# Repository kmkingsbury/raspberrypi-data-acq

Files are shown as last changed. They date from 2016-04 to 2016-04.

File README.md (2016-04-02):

# raspberrypi-data-acq

Scripts for using a Raspberry Pi 2 B+ as a data acquisition box.
Instructable for this project: http://www.instructables.com/id/Scrappy-Science-Caddy

## Supported Platforms

Raspberry Pi 2 B+

## Attributes

<table>
  <tr>
    <th>Key</th>
    <th>Type</th>
    <th>Description</th>
  </tr>
  <tr>
    <td><tt>-s,--sleep</tt></td>
    <td>Float</td>
    <td>Time to sleep between measurements. Like a polling frequency, if set to 1 it will take a new measurement roughly every second, .5 is every half second, etc.</td>
  </tr>
  <tr>
    <td><tt>-n,--channels</tt></td>
    <td>Integer</td>
    <td>Number of channels to record</td>
  </tr>
  <tr>
    <td><tt>-g,--gnuplot</tt></td>
    <td>Switch</td>
    <td>Output the file in a GNUPlot-friendly format rather than a CSV</td>
  </tr>
  <tr>
    <td><tt>-c,--config</tt></td>
    <td>String</td>
    <td>Use Config file, default config.ini</td>
  </tr>
  <tr>
    <td><tt>-o,--outfile</tt></td>
    <td>String</td>
    <td>CSV Output file to use</td>
  </tr>
  <tr>
    <td><tt>-d,--debug</tt></td>
    <td>String</td>
    <td>Output extra messages for debugging</td>
  </tr>
  <tr>
    <td><tt>-t,--type</tt></td>
    <td>String</td>
    <td>Data Type for each channel. (See explanation below)</td>
  </tr>
</table>

### Data Type

Data type is the type of data coming on the channel, automatic conversions can ve done. If none specified then it uses 'raw' as the default which is the straight reading from the GPIO pin (values 0-1024). Other supported types are 'ctemp' which converts the value to a Temperature in Celsius, and 'ftype' which converts the value to a Temperature in Fahrenheit. Data types can be mixed and matched, assume a three channel setup, you could do raw for the first channel, ctemp for the 2nd and ftemp for the third. Such a setup would look like:

```python
sudo python collectdata.py -c 3 -t raw ctemp ftemp
```

## Usage

Basic Program flow:
* Specify the number of channels, output file, and/or any other parameters.
* The script runs indefinitely logging data to the output file and displaying on screen
* Use Ctrl-C to quit.

### python collectdata.py

Run normally using all defaults:
```python
raspberrypi-data-acq $ sudo python ./collectdata.py
```

Record data from 4 different sources:
```python
raspberrypi-data-acq $ sudo python ./collectdata.py -c 4
```

Record data from 4 different sources at 1/10 of a second intervals:
```python
raspberrypi-data-acq $ sudo python ./collectdata.py -c 4 -s 0.1
```

Record data from 4 different sources at 1/10 of a second intervals, output to mydata.csv in the home directory:
```python
raspberrypi-data-acq $ sudo python ./collectdata.py -c 4 -s 0.1 -o ~/mydata.csv
```

Record data from 3 different sources the first as raw data, Celsius Temperature for the 2nd and 3rd:
```python
raspberrypi-data-acq $ sudo python ./collectdata.py -c 3 -t raw ctemp ctemp
```

## Pi Configuration
usbmount is used to automount a USB stick when it is plugged in, install the package:
```
sudo apt-get install usbmount
```

Configuration in /etc/usbmount/usbmount.conf

Files are then by default dropped in ```/media/usb0```

## License and Authors

Author:: Kevin Kingsbury (@kmkingsbury)

Apache 2.0

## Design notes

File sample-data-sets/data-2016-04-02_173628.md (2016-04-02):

Raw parameters: collectdata.py -n 4 -s .1 -g
Namespace parameters: collectdata.py Namespace(channels=[4], config=None, debug=False, gnuplot=True, outfile=None, sleep=[0.1], type=None)
Config file: config.ini
Channels: 4
Sleeptime: 0.1
Types: [raw, raw, raw, raw]
DataTypes: [raw, raw, raw, raw]
Samples: 20607
ButtonEvents: 0
Avg: [121, 132, 158, 176]
Maxs: [327, 329, 377, 405]
Mins: [0, 0, 0, 0]

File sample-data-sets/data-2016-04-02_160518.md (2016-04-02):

Raw parameters: collectdata.py -n 1 -s .25 -g
Namespace parameters: collectdata.py Namespace(channels=[1], config=None, debug=False, gnuplot=True, outfile=None, sleep=[0.25], type=None)
Config file: config.ini
Channels: 1
Sleeptime: 0.25
Types: [raw]
DataTypes: [raw]
mk3 Event: 2016-04-02 16:17:24.08, 318
mk2 Event: 2016-04-02 16:24:20.52,411
mk1 Event: 2016-04-02 16:23:36.10,402
mk4 Event: 2016-04-02 16:33:35.97,428
mk4 Event: 2016-04-02 16:57:30.68,365
Samples: 11917
ButtonEvents: 5
Avg: [363]
Maxs: [468]
Mins: [217]

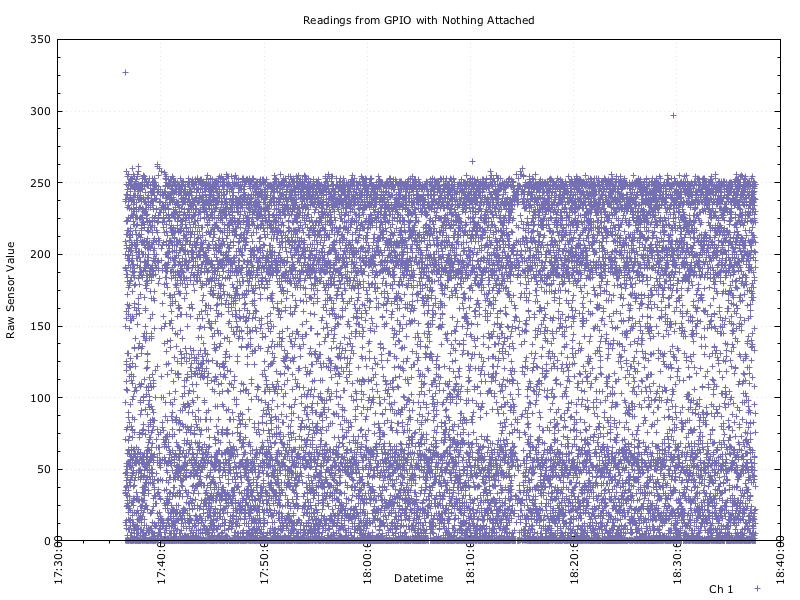
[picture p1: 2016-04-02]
sample-data-sets/data-2016-04-02_173628.gnuplot_raw.png

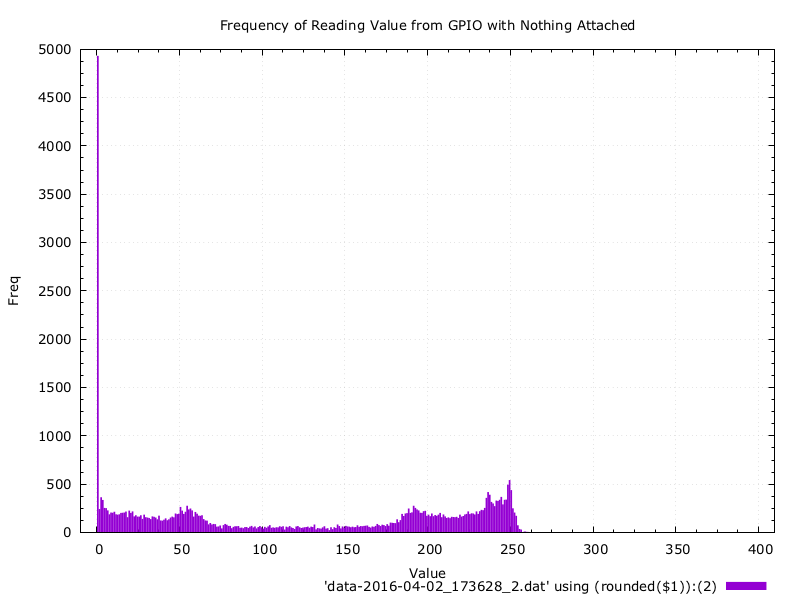
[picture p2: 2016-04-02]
sample-data-sets/data-2016-04-02_173628.gnuplot_freq.png

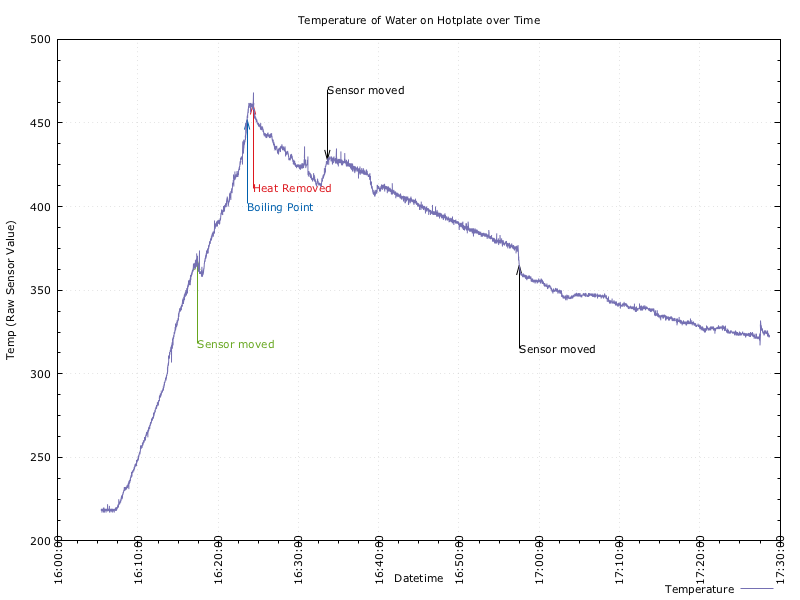
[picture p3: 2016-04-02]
sample-data-sets/data-2016-04-02_160518.gnuplot.png

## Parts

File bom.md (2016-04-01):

# Bill of Materials

## Hardware
Item|Count|Price|Url / Source
----|-----|-----|------------
Red Oak Hobby Board (Common: 1/4-in x 6-in x 2-Ft; Actual: 0.25-in x 5.5-in x 2-ft)| 1|$6.47|http://www.lowes.com/pd_9365-34050-OAK6X140-U2S___
Plexiglass sheet |1|$2.97|http://www.lowes.com/pd_55844-1638-11G0810A___
Motherboard mounts|8|$7.90 (for 50)|http://amzn.com/B00008VF6K
Round-Head Standard (SAE) Machine Screws #4 & #6 size |~16|$1.24 for 12 |http://www.lowes.com/pd_62045-37672-491276___
Nylon Standoffs|8|~$2.00|Local Big Box Store

## Electronics
Item|Count|Price|Url / Source
----|-----|-----|------------
Raspberry Pi 2 or 3 |1|$37.99 or $45.97|http://amzn.com/B018L66L9S or http://amzn.com/B01CD5VC92
MCP3008 |1|$3.75 |https://www.adafruit.com/product/856
Push Buttons (green, black, red, blue)|4|$6.98 (for 10 in one color)| http://amzn.com/B015CYF3VE, http://amzn.com/B015CYHS3U, http://amzn.com/B015CY8WJ4, http://amzn.com/B017EFQD6S
5 way navigation button |1|$2.95 | https://www.adafruit.com/products/504
Poteniometer |1 | $1.25|https://www.adafruit.com/products/356
LCD 16x2 Char Display |1|$15.95 |https://www.sparkfun.com/products/709
3 pin polarized connector (Male & Female) | 4| $0.50| http://www.kr4.us/polarized-connectors-housing-3-pin.html
Optional: 16 Pins Round Hole DIP IC Chip Socket Adaptor | 1| $5.16 (for 10)|http://amzn.com/B00X77NYG0
Optional: PCB Board 16 Pin |1 | 7.11 (for 20)| http://amzn.com/B01173BKZW (I got mine for $2 at Radioshack)

----
## Assorted Odds &amp; Ends on Hand
* Hook-up Wire
* Paint & Primer (or wood stain)
* Wood Glue
* Small nails
* Wire shrink wraps
* Electrical Tape
* Old IDE Cable for pins (http://amzn.com/B002BBNEOU)
* Motherboard mounts (also listed above)
* Screws #4 & #6 (also listed above)

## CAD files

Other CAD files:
drawings/data-container.skp

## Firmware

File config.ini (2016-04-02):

[general]
# include trailing slash
filesavedir = /media/usb0/

[AD MCP3008]
# Analog to Digital Converter Chip MCP3008
SPICLK = 18
SPIMISO = 23
SPIMOSI = 24
SPICS = 25

[menu]
# 5-way navigation (next to LCD)
up =  22
down = 27
left = 17
right = 7
select = 4

[buttons]
# Push buttons on top: Red, Green, Blue, Black
Mk1 = 13
MK2 = 6
Mk3 = 5
Mk4 = 8

[lcd]
# LCD Control Pins
LCD_RS = 19
LCD_E  = 26
LCD_D4 = 20
LCD_D5 = 16
LCD_D6 = 12
LCD_D7 = 21
LCD_WIDTH = 16
# Maximum characters per line
LCD_CHR = true
LCD_CMD = false
# LCD RAM address for the 1st line
LCD_LINE_1 = 0x80
# LCD RAM address for the 2nd line
LCD_LINE_2 = 0xC0

# Timing constants
E_PULSE = 0.0005
E_DELAY = 0.0005

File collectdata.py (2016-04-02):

#! /usr/bin/python
# Based off the daemon code written by Dan Mandle http://dan.mandle.me September 2012
# LCD parts from 16x2 LCD Test Script
# which is written by : Matt Hawkins 06/04/2015 (http://www.raspberrypi-spy.co.uk/)
#
# The Rest by Kevin Kingsbury: https://github.com/kmkingsbury
# License: Apache 2.0

import os
from daemon import Daemon
from subprocess import *
import RPi.GPIO as GPIO

import time
from time import gmtime, strftime
import threading
#import yaml
import csv
#import rrdtool
import sys, argparse
import ConfigParser
import re

from ssc_lcd import *

version = 0.1

class SmartFormatter(argparse.HelpFormatter):

    def _split_lines(self, text, width):
        # this is the RawTextHelpFormatter._split_lines
        if text.startswith('R|'):
            return text[2:].splitlines()
        return argparse.HelpFormatter._split_lines(self, text, width)

GPIO.setwarnings(False)
GPIO.setmode(GPIO.BCM)


# Parse Args:
def mainargs(argv):
  parser = argparse.ArgumentParser(description='Collects Data on a Raspberry Pi 2 B+.',
  formatter_class=SmartFormatter, epilog="Example 3 channel of raw and 2 Celsius temperature:\n sudo python ./collectdata.py -n 3 -t raw ctemp ctemp"
  )
  parser.add_argument('-s', '--sleep', type=float, nargs=1, required=False,
                   help='Time (seconds) to sleep between measurements')
  parser.add_argument('-n', '--channels', type=int, nargs=1, required=False,
                 help='Number of channels to record')
  parser.add_argument('-o', '--outfile', nargs=1, required=False,
               help='Outfile to use')
  parser.add_argument('-c', '--config', nargs=1, required=False,
                            help='Config File to use')
  parser.add_argument('-g', '--gnuplot', action='store_true', required=False,
               help='Print the outputfile in gnuplot format (tabs) instead of CSV')
  parser.add_argument('-d', '--debug', action='store_true', required=False,
               help='Print Debug messages')
  parser.add_argument('-t', '--type', type=str, nargs='+', required=False, choices=['raw', 'ctemp', 'ftemp'],
               help="R|Datatypes to record space separate.\n"
         " raw = raw values (0 to 1024, default value)\n"
         " ctemp = Temperature (Celsius)\n"
         " ftemp = Temperature (Fahrenheit)")
  args = parser.parse_args()
  return args

def run_cmd(cmd):
    p = Popen(cmd, shell=True, stdout=PIPE)
    output = p.communicate()[0]
    return output

def CtoF(temp):
	temp = (temp * (9.0/5.0))+32.0
	return round(temp,2)

def ConvertTemp(data):
	temp = ((data - 100)/10.0) - 40.0
	temp = round(temp,4)
	return temp

def ConvertmVolts(data):
	volts = (data * 3300.0) / 1023.0
	volts = round(volts, 4)
	return volts

def buttonEventHandler (pin):
    global config, fpmeta, displaymode, MKbuttonevents, data
    print "handling button event: "+str(pin)

    # Match Buttons, Log event:
    for (each_key, each_val) in config.items('buttons'):
      if pin == int(each_val):
        #print "here.\n"
        timenow = highrestime()
        fpmeta.write(""+each_key + ' Event: '+ timenow + ', '.join(map(str, data)) + '\n')
        MKbuttonevents += 1
        return

    # Match Menu
    if pin == config.getint('menu', 'up'):
      displaymode = 'Max'
      return
    elif pin == config.getint('menu', 'down'):
      displaymode = 'Min'
      return
    elif pin == config.getint('menu', 'right'):
      displaymode = 'Avg'
      return
    elif pin == config.getint('menu', 'left'):
      displaymode = 'Dev'
      return
    elif pin == config.getint('menu', 'select'):
      displaymode = 'Reg'
      return


def highrestime():
    global time
    mynow = str(time.time())
    timenow = strftime("%Y-%m-%d %H:%M:%S", gmtime())
    dec = mynow.split(".")
    #this is a dumb way to get zero padded decimal seconds
    timenow += "."+format(float("."+dec[1]), '.2f').split('.')[1]
    return timenow

# read SPI data from MCP3008 chip, 8 possible adc's (0 thru 7)
def readadc(adcnum, clockpin, mosipin, misopin, cspin):
        if ((adcnum > 7) or (adcnum < 0)):
                return -1
        GPIO.output(cspin, True)

        GPIO.output(clockpin, False)  # start clock low
        GPIO.output(cspin, False)     # bring CS low

        commandout = adcnum
        commandout |= 0x18  # start bit + single-ended bit
        commandout <<= 3    # we only need to send 5 bits here
        for i in range(5):
                if (commandout & 0x80):
                        GPIO.output(mosipin, True)
                else:
                        GPIO.output(mosipin, False)
                commandout <<= 1
                GPIO.output(clockpin, True)
                GPIO.output(clockpin, False)

        adcout = 0
        # read in one empty bit, one null bit and 10 ADC bits
        for i in range(12):
                GPIO.output(clockpin, True)
                GPIO.output(clockpin, False)
                adcout <<= 1
                if (GPIO.input(misopin)):
                        adcout |= 0x1

        GPIO.output(cspin, True)

        adcout >>= 1       # first bit is 'null' so drop it
        return adcout

rawargs = ' '.join (sys.argv)
#print "Raw: "+ rawargs

# Parse Args, handle options
args = mainargs(sys.argv[1:])

# Config File
configfile = 'config.ini'
if args.config: config = args.config[0]
if args.debug: print "Config file: " + str(configfile)

config = ConfigParser.ConfigParser()
config.read(configfile)

# Sleep
sleeptime = 1;
if args.sleep: sleeptime = args.sleep[0]
if args.debug: print "Sleep time: " + str(sleeptime)

# Channels
channels = 4;
if args.channels: channels = int(args.channels[0])
if args.debug: print "Channels: " + str(channels)

# Outfile
outfile = config.get('general', 'filesavedir', 0) + "data-"+strftime("%Y-%m-%d_%H%M%S", gmtime())+".csv"
if args.gnuplot: outfile = "data-"+strftime("%Y-%m-%d_%H%M%S", gmtime())+".dat"
if args.outfile: outfile = args.outfile[0]
if args.debug: print "Outfile: " + outfile
filewoext = re.split('(.*)\.\w', outfile)
#print filewoext[1]
metafile = filewoext[1] +".md"
if args.debug: print "Metafile: "+ metafile

# This is all matching the datatypes and getting the correct array sizes
types = []
if args.type:
  types = args.type
else:
  types = ['raw'] * channels

datatype = ['raw'] * 8
if args.debug: print "Len:" + str(len(types))
if len(types) != channels:
  for val in range(0,channels):
    if args.debug: print "Vals: " + str(val)
    try:
      #print "DT (" + str(val) + "):" + str(datatype[val-1] )
      if args.debug: print "T (" + str(val) + "):" + str(types[val] )

      datatype[(val)] = types[val]
    except IndexError:
      datatype.append('raw')
elif len(types) > channels:
  datatype = types[:(channels)]
else:
  datatype = types[:(channels)]

# make final correct size
datatype = datatype[:(channels)]
if args.debug: print "Types: " + '[%s]' % ', '.join(map(str, types))
if args.debug: print "DataTypes: " + '[%s]' % ', '.join(map(str, datatype))


# put in top level scope, reset in the loop

if __name__ == '__main__':

  runner = True

  print 'sys:'+ str(sys.argv[0]) + ' ' + str(args)

  # Logger open CSV
  fp = open(outfile, 'w')
  fpmeta = open(metafile, 'w')
  fpmeta.write('Raw parameters: '+rawargs+ '\n')
  fpmeta.write('Namespace parameters: '+ str(sys.argv[0]) + ' ' + str(args) + '\n')
  fpmeta.write('Config file: ' + str(configfile) + '\n')
  fpmeta.write('Channels: ' + str(channels)+ '\n')
  fpmeta.write('Sleeptime: ' + str(sleeptime)+ '\n')
  fpmeta.write("Types: " + '[%s]' % ', '.join(map(str, types))+ '\n')
  fpmeta.write("DataTypes: " + '[%s]' % ', '.join(map(str, datatype))+ '\n')

  fp.write('# Input parameters: '+ str(sys.argv[0]) + ' ' + str(args) + '\n')
  fp.write('# Datetime\t\t')
  for x in range(1, channels):
      fp.write("\t Ch"+str(x))
  fp.write("\n")

  cvs = None
  if args.gnuplot == False:
    writer = csv.DictWriter(fp, fieldnames = ['datetime']+ datatype, delimiter=',')
    writer.writeheader()
    csv = csv.writer(fp, delimiter=',', quoting=csv.QUOTE_ALL)
  else:
    csv = csv.writer(fp, delimiter="\t", quoting=csv.QUOTE_NONNUMERIC, quotechar='\'')

  # set up the SPI interface pins
  GPIO.setup(config.getint('AD MCP3008', 'SPIMOSI'), GPIO.OUT)
  GPIO.setup(config.getint('AD MCP3008', 'SPIMISO'), GPIO.IN)
  GPIO.setup(config.getint('AD MCP3008', 'SPICLK'), GPIO.OUT)
  GPIO.setup(config.getint('AD MCP3008', 'SPICS'), GPIO.OUT)

  GPIO.setup(config.getint('lcd', 'LCD_RS'), GPIO.OUT)
  GPIO.setup(config.getint('lcd', 'LCD_E'), GPIO.OUT)
  GPIO.setup(config.getint('lcd', 'LCD_D4'), GPIO.OUT)
  GPIO.setup(config.getint('lcd', 'LCD_D5'), GPIO.OUT)
  GPIO.setup(config.getint('lcd', 'LCD_D6'), GPIO.OUT)
  GPIO.setup(config.getint('lcd', 'LCD_D7'), GPIO.OUT)


  lcd_init(config)
  lcd_string(config,"Scrapy Science",0x80)
  lcd_string(config,"Caddy v"+str(version),0xC0)
  time.sleep(2)
  lcd_string(config,strftime("%Y-%m-%d %H:%M", gmtime()),0x80)
  cmd = "ip addr show wlan0 | grep inet | awk '{print $2}' | cut -d/ -f1 | head -n 1"
  ipaddr = run_cmd(cmd).strip()
  lcd_string(config,ipaddr,0xC0)
  time.sleep(2)

  # Button Setups:
  for (each_key, each_val) in config.items('menu'):
    GPIO.setup(int(each_val), GPIO.IN, pull_up_down=GPIO.PUD_UP)
    GPIO.add_event_detect(int(each_val),GPIO.FALLING, callback=buttonEventHandler, bouncetime=300)

  for (each_key, each_val) in config.items('buttons'):
    GPIO.setup(int(each_val), GPIO.IN, pull_up_down=GPIO.PUD_UP)
    GPIO.add_event_detect(int(each_val), GPIO.FALLING, callback=buttonEventHandler, bouncetime=300)

  # Reset count
  samplecount = 0
  MKbuttonevents = 0
  lastgmt = 0
  displaymode = 'Reg'
  sums = [0,0,0,0];
  mins = [None, None, None, None]
  maxs = [None, None, None, None]
  avgs = [0,0,0,0];
  try:
    while (runner == True):
      #It may take a second or two to get good data

      timenow = highrestime()
      data = [ timenow,0,0,0,0,0,0,0,0 ]
      rawvalues = [0] * 8
      values = [0] * 8
      for val in range(0,channels):
       if args.debug: print "Val:" + str(val)
       rawvalues[val] = readadc(val,
        config.getint('AD MCP3008', 'SPICLK'),
        config.getint('AD MCP3008', 'SPIMOSI'),
        config.getint('AD MCP3008', 'SPIMISO'),
        config.getint('AD MCP3008', 'SPICS'))

       # Convert raw value to something else if specificed in type option.
       if datatype[(val)] == 'ftemp':
         values[val] = CtoF(ConvertTemp(ConvertmVolts(rawvalues[val])))
       elif datatype[(val)] == 'ctemp':
         values[val] = ConvertTemp(ConvertmVolts(rawvalues[val]))
       else:
         values[val] = rawvalues[val]
       data[(val+1)] = values[val]
       sums[val] += values[val]
       if mins[val] == None : mins[val] = values[val]
       if maxs[val] == None : maxs[val] = values[val]
       if values[val] < mins[val]: mins[val] = values[val]
       if values[val] > maxs[val]: maxs[val] = values[val]
       avgs[val] = sums[val]/(samplecount+1)
      # Prepare and Print the raw values if debug flag set
      rawline = 'Raw '
      for val in range(0,channels):
        rawline += "V"+str(val+1)+":"+ str(rawvalues[val]) + " "
      if args.debug: print rawline
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

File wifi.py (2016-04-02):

import ConfigParser
import os
import time

from time import gmtime, strftime
from subprocess import *
import RPi.GPIO as GPIO

from ssc_lcd import *

configfile = 'config.ini'

config = ConfigParser.ConfigParser()
config.read(configfile)

GPIO.setwarnings(False)
GPIO.setmode(GPIO.BCM)
GPIO.setup(config.getint('lcd', 'LCD_RS'), GPIO.OUT)
GPIO.setup(config.getint('lcd', 'LCD_E'), GPIO.OUT)
GPIO.setup(config.getint('lcd', 'LCD_D4'), GPIO.OUT)
GPIO.setup(config.getint('lcd', 'LCD_D5'), GPIO.OUT)
GPIO.setup(config.getint('lcd', 'LCD_D6'), GPIO.OUT)
GPIO.setup(config.getint('lcd', 'LCD_D7'), GPIO.OUT)


def run_cmd(cmd):
    p = Popen(cmd, shell=True, stdout=PIPE)
    output = p.communicate()[0]
    return output

try:
    while (1 == 1):
      lcd_string(config,strftime("%Y-%m-%d %H:%M", gmtime()),0x80)
      cmd = "ip addr show wlan0 | grep inet | awk '{print $2}' | cut -d/ -f1 | head -n 1"
      ipaddr = run_cmd(cmd).strip()
      lcd_string(config,ipaddr,0xC0)
      time.sleep(2)

except (KeyboardInterrupt, SystemExit): #when you press ctrl+c
  print "\nKilling Thread..."
  lcd_byte(config,0x01, config.getboolean('lcd', 'LCD_CMD'))
  lcd_string(config,"Goodbye",0x80)
  lcd_string(config,ipaddr,0xC0)
  GPIO.cleanup()
  exit();

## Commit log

2015-09-15 Added current sketchup drawing
    [data-container.skp]
2015-09-15 Added schematic folder and Fritzing Diagram
    [Data-Acq.fzz]
2015-09-26 Pin setup
2016-02-11 Expanded the help file, added sample data sets.
    [temp-temp-soil.csv, temp-temp-soil2.csv]
2016-02-18 Updated drawing, added objects
    [data-container.skp]
2016-03-17 Updated drawing, added wiring and buttons to schematic
    [Data-Acq.fzz, data-container.skp]
2016-03-25 Updated drawings, added in BOM.md too
    [Data-Acq.fzz, data-container.skp]
2016-03-31 Added 3 pin connectors
2016-04-01 Changed default filename, added IC sockets to BOM
2016-04-02 Added simple script wifi.py which loops and prints IP addr
